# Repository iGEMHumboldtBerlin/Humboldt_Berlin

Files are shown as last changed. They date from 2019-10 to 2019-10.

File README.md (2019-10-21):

# Humboldt_Berlin

README

The openPBR is a low-cost, easy to assemble and reliable option to cultivate phototrophic organisms. We have developed it as an open-source platform to operate as you need it. It comes in several setups, from nine cultivation vessels to three flat panels with a minimum width of 15 mm and up to a volume of 190 ml. It provides users with the ability to measure optical density at wavelengths from 400 nm to 800 nm, online and provides a .csv file output. All parts are openly available and even gas supply is exactly adjustable through a rotameter, depending on the needs of your organism and setup. We want to offer scientists a simple and versatile cultivation platform.

################
Design and development by Paul Herrmann

The openPBR is controlled by one single Arduino script, which enables by varying 9 variables full control of all parameters. 
These variables are for light, pumping time (one for each pump), interval of measurement and wished OD of dilution.

To get the output of the openPBR use the free serial log program PuTTY: https://www.chiark.greenend.org.uk/~sgtatham/putty/latest.html and save as a .csv.

The current code on _v0.1 is for 3 sensors. 

User manual:
1. Start the Arduino IDE open the openPBR_control
2. Select the COM of the Arduino
3. Choose your settings:

For the light color and intensity set the value between 0 and 255 in line White line 91, Red line 92,Green 93,Blue 94 for the according color.

To adjust the interval of measurement, type a value between 30000 and 1000000 in line 99. This value is given in milliseconds so one minute is 60000 milliseconds.

To adjust the run time of the pumps set the value in line 100 from (milliseconds).
The value for the OD that starts the pumping can be set for every chamber starting at line 383. (example OD 1 [a.u.] = 0.95v on Vout of opt101. Divide 1024 by 5 volt times the Vout value you want to dilute the culture by)
 
4. Upload the code to the Arduino
5. Start PuTTy and Select the COM of the Arduino
6. Choose the output file folder and and give your .csv a name.
7. Start PuTTy logging.
8. Close PuTTy and the values are stored in the .csv file.

How to convert the values into OD, see Calibration openPBR DIY step by step on GitHub.

For help contact: igemberl@hu-berlin.de 

README

The openPBR is a low-cost, easy to assemble and reliable option to cultivate phototrophic organisms. We have developed it as an open-source platform to operate as you need it. It comes in several setups, from nine cultivation vessels to three flat panels with a minimum width of 15 mm and up to a volume of 190 ml. It provides users with the ability to measure optical density at wavelengths from 400 nm to 800 nm, online and provides a .csv file output. All parts are openly available and even gas supply is exactly adjustable through a rotameter, depending on the needs of your organism and setup. We want to offer scientists a simple and versatile cultivation platform.

################
Design and development by Paul Herrmann

The openPBR is controlled by one single Arduino script, which enables by varying 9 variables full control of all parameters. 
These variables are for light, pumping time (one for each pump), interval of measurement and wished OD of dilution.
To get the output of the openPBR the free serial log program PuTTY: https://www.chiark.greenend.org.uk/~sgtatham/putty/latest.html

User manual:

The current code on _v0.1 is for 3 sensors. 

1. Start the Arduino IDE open the openPBR_control
2. Select the COM of the Arduino
3. Choose your settings:

For the light color and intensity set the value between 0 and 255 in line 91 for the according color.

brightnessWhite = 150;
brightnessRed = 150;
brightnessGreen = 150;
brightnessBlue = 150; 

To adjust the interval of measurement change:

const long interval = 10*60*1000; // 10 minutes x 60 sec * 1000 milli 

To adjust the run time of the pumps set the value in line 100 from 

const int pumpTime = 5000; // time the pump is running

The value for the OD that starts the pumping can be set for every chamber starting at line 383. (example OD 1 [a.u.] = 0.95v on Vout of opt101. Divide 1024 by 5 volt times the Vout value you want to dilute the culture by)
 
4. Upload the code to the Arduino
5. Start PuTTy and Select the COM of the Arduino
6. Choose the output file folder and and give your .csv a name.
7. Start PuTTy logging.
8. Close PuTTy and the values are stored in the .csv file.

How to convert the values into OD, see Calibration openPBR DIY step by step on GitHub.

For help contact: igemberl@hu-berlin.de

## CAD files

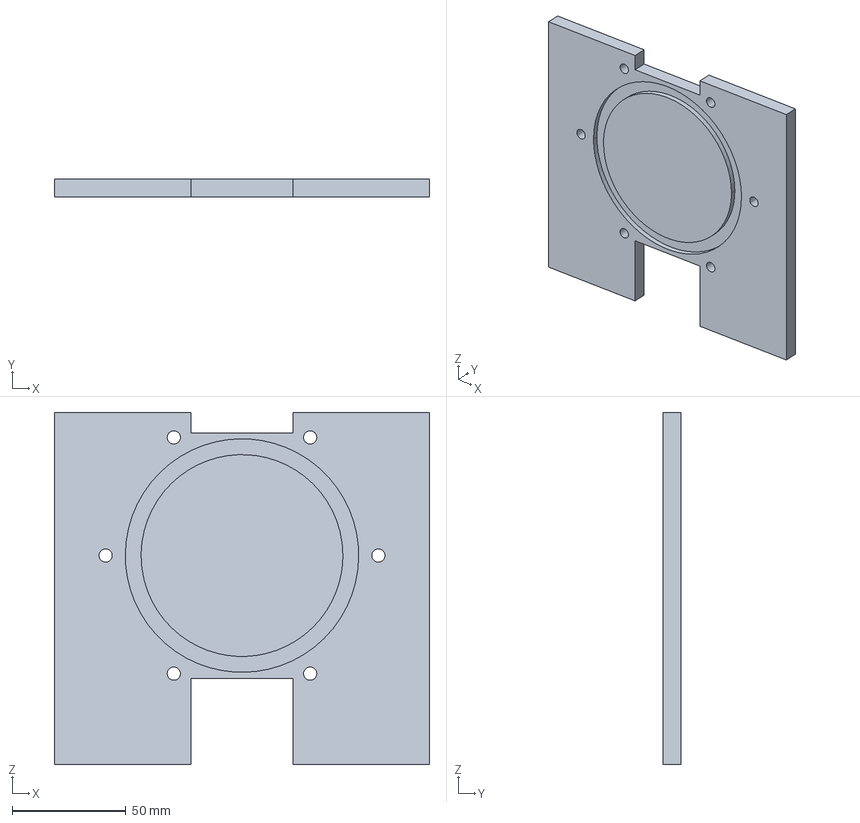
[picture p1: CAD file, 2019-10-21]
Laser cut files/Flat panel groove_02.stp
165.0 x 8.00 x 155.0 mm

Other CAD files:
CAD Models/openPBR_ laser cut_v0.1.dwg
Laser cut files/openPBR_lasercut_v0.1.dwg

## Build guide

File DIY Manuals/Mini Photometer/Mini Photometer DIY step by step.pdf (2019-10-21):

Introduction

To perform our needed functions, we build a small low-cost DIY photometer which can measure the optical density (OD) at 680 nm or any other wavelength in the visible spectrum. The photometer is designed to not only work inside our cultivation setup, but can also be used as a stand-alone solution for OD measurement.

Photometer
This is a small do it yourself photometer, using the light sensor Opt101 from Texas Instruments. It measures the absorption at 680nm of a given solution or cell culture as optical density (OD).
Parts List:
- Monolithic linear ambient light sensor Opt101
- LED 680nm (or else in visible light)
- 2 standard cuvettes
- Arduino with USB cable
- 2x 1kohm, 2x 10ohm,1x 5kohm resistors (optional potentiometer)
- Cables
- Two steel plates 80x10x1mm with two 3mm holes and a 50mm slit.
- 3x 3mm screws and nuts.
- optional 1-2 spacer (12mm long steel pipe)
- Breadboard
- Cardboard box
Software:
- Arduino IDE
- Putty (for serial monitor to csv file)
- Code for the photometer

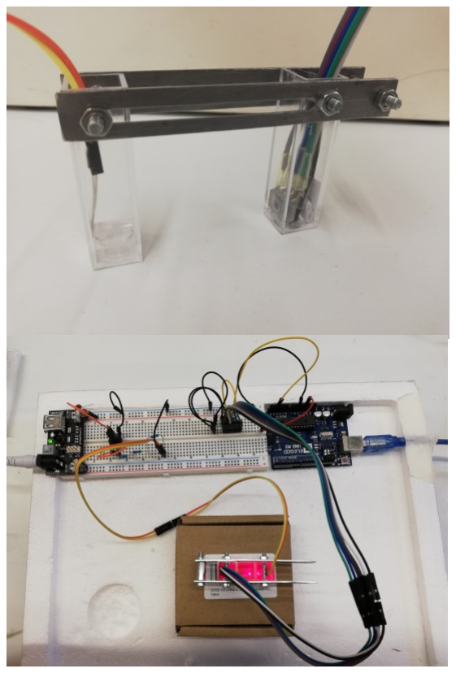
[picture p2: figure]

# Cost list and links:

LED680-02AU, 680 nm, 25 mW/sr, 4 mW at 20 mA, ±7°, 5 mm clear epoxy http://www.roithner-laser.com/datasheets/led_div/led680-series.pdf 3,98 Euro
OPT101 Lightsensor linear VIS IR Photodiode 300nm-1100nm 2,7-36V Sensor Modul https://www.amazon.de/gp/product/B07WHTF4S9/ref=ppx_yo_dt_b_asin_title_o00_s00?ie=UTF8&psc=1 (https://www.amazon.de/gp/product/B07WHTF4S9/ref=ppx_yo_dt_b_asin_title_o00_s00?ie=UTF8&psc=1) 4,97 Euro
ARDUINO UNO REV 3
https://www.amazon.de/Arduino-Uno-Rev-3-Mikrocontroller-Board/dp/B008GRTSV6/ref=sr_1_4?__mk_de_DE=%C3%85M%C3%85%C5%BD%C3%95%C3%91&keywords=Arduino&qid=1570469452&s=industrial&sr=1-4 (https://www.amazon.de/Arduino-Uno-Rev-3-Mikrocontroller-Board/dp/B008GRTSV6?__mk_de_DE=%C3%85M%C3%85%C5%BD%C3%95%C3%91&s=industrial) 17,89 Euro
Total: ~ 27 Euro

We would recommend buying an Arduino set with a lot of other fun parts and everything you need like cables and resistors.
ELEGOO UNO R3 Ultimate Starter Kit https://www.amazon.de/Elegoo-Vollst%C3%A4ndige-Ultimate-Tutorial-Mikrocontroller/dp/B01IHCCKKK?ref_=ast_sto_dp (https://www.amazon.de/Elegoo-Vollst%C3%A4ndige-Ultimate-Tutorial-Mikrocontroller/dp/B01IHCCKKK) 46,99 Euro

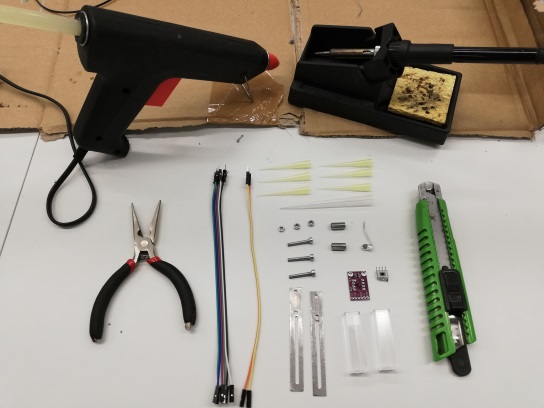
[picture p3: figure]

Tools:
- soldering iron
- Knife
- Tongs
- Hot glue (optional)

Assembling of the parts.
1.Prepare the LED attachment with a 1ml Pipet tip. Put the LED in the middle part of the pipet tip
that should be around 10mm long and stick in
to the cuvette. Paper on the sides helps to
center the LED.

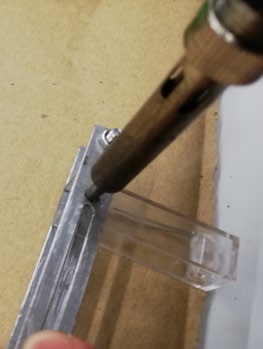
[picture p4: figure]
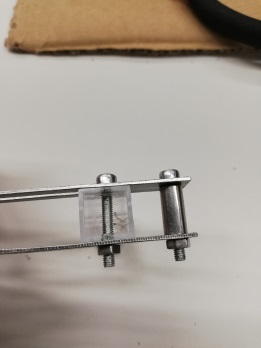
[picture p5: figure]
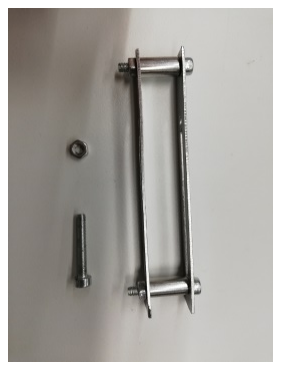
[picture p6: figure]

2. Assemble the cuvette holding and burn holes in the cuvettes with the soldering iron. Put the screw to the holes and fix them with the nuts.

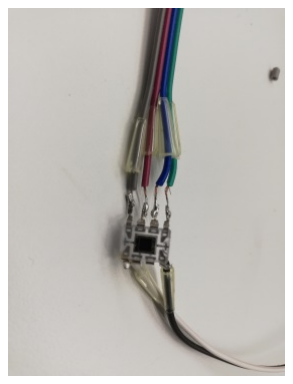
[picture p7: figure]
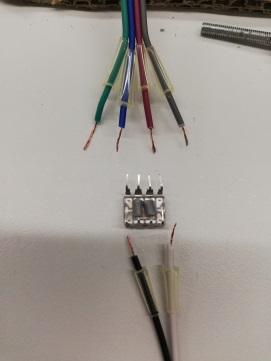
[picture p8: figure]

3. Prepare cables and something to protect the contacts for example 200µl pipet tips. Solder the cables to the Opt101.

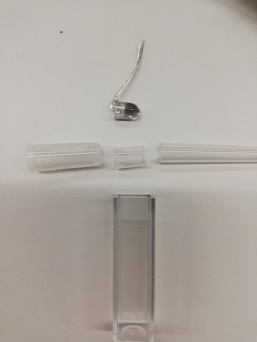
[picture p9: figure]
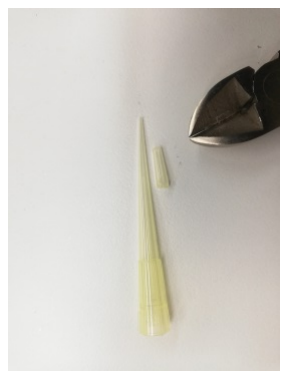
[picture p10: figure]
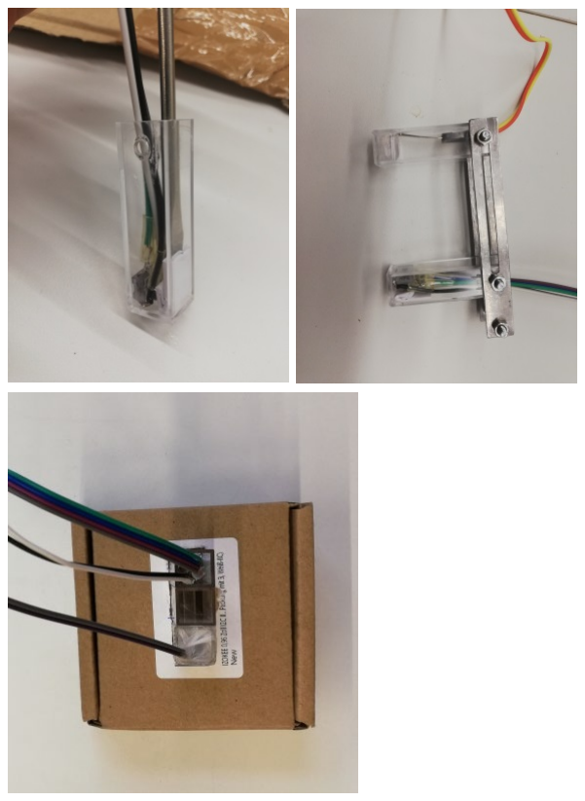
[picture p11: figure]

4. Insert the Opt 101 in to its cuvette and screw it in the cuvette holder. Add some paper so it stays in place and fits tight.
7. Cut out a hole in a cardboard box and put the photometer in.

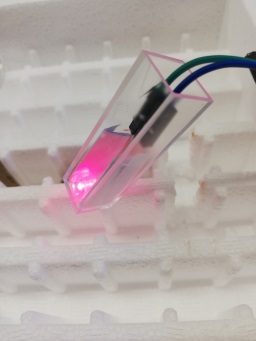
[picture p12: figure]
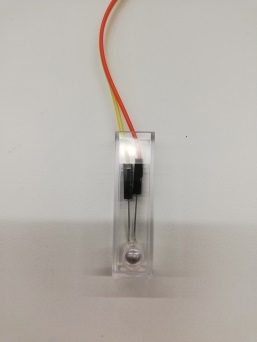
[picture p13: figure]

Wiring of the Opt101 to the Arduino. Connect the cables to the Opt101 as following: 1: green 5/3,3V (VCC)
3: black to GND
2: blue, 4: grey, 5: white over a 1M ohm resistor to Output 8: violet to GND
6 and 7 to nothing.

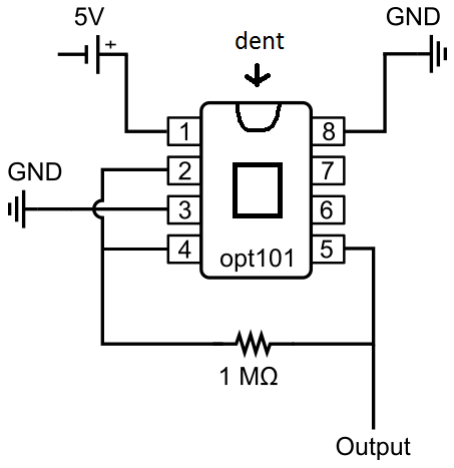
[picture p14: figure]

The sensor has a dent on one side this shows the orientation. It should look like this:

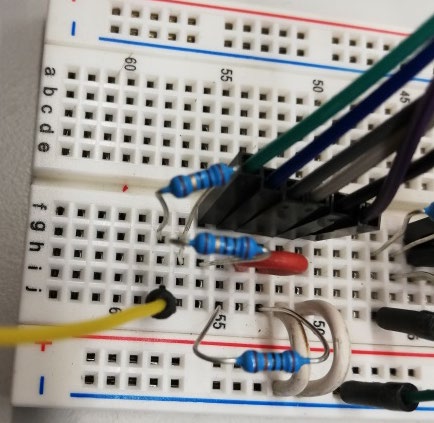
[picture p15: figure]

- Connect the Output (orange) and
a cable to monitor the current (red) to an analog pin (A0, A3) as well as the 5V (yellow) to the Arduino. Connect a cable (black) to GND.

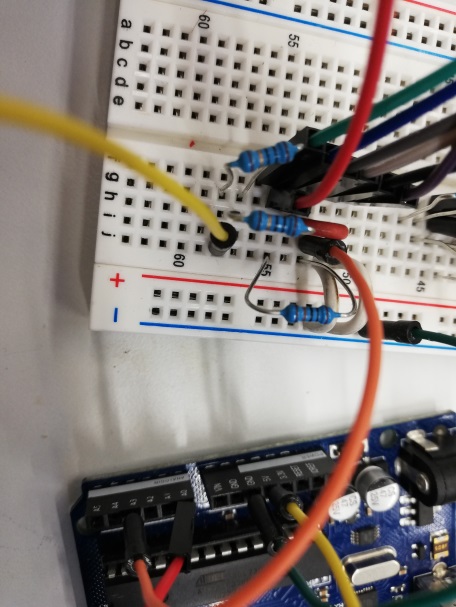
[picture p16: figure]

- For the 680nm LED connect a cable to 5V and put one 1 kohm and a 5 kohm resistor in a row to generate ~1.4 kohm resistance. This depends on the distance between LED and sensor as to the LED itself so it will differ from setup to setup. You can also put a Potentiometer instead of the resistor to find out which resistance fits for your setup. But don’t give the LED 5V, OR IT WILL BURST!

## Calibration of the Opt101

Prepare a dilution series of your Algae in this case C. reinhardtii. And measure it with a at 680 nm photometer.

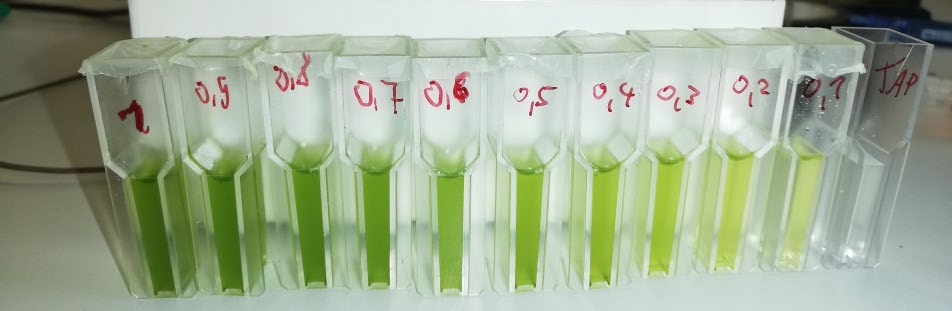
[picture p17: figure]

1. To calibrate the sensors set up a decadal dilution series of a given OD (from a reference photometer) from OD 2.5 down do OD 0.1.
2. Set the interval in the openPBR_control to 30 seconds
3. Start PuTTY and measure a single data point for each step of the dilution.
4. Include the data in to a excel file.

In order to get a net voltage, you need to subtract the output value from the input value. Subtract the Vout values from the Vin values and plot them against the reference OD from your photometer. Then perform a logarithmic fit (Fig. 1)

Your equation should look something like this: ∆VV = aa ∗ log(OOOO) + bb

In our example we got a = 0.496 and b = 4.389.

In this case, y is the voltage ∆V and x the OD.

To get the OD from your measured values, solve your equation for x:

# xx = ee

# ∆VV−bb

aa

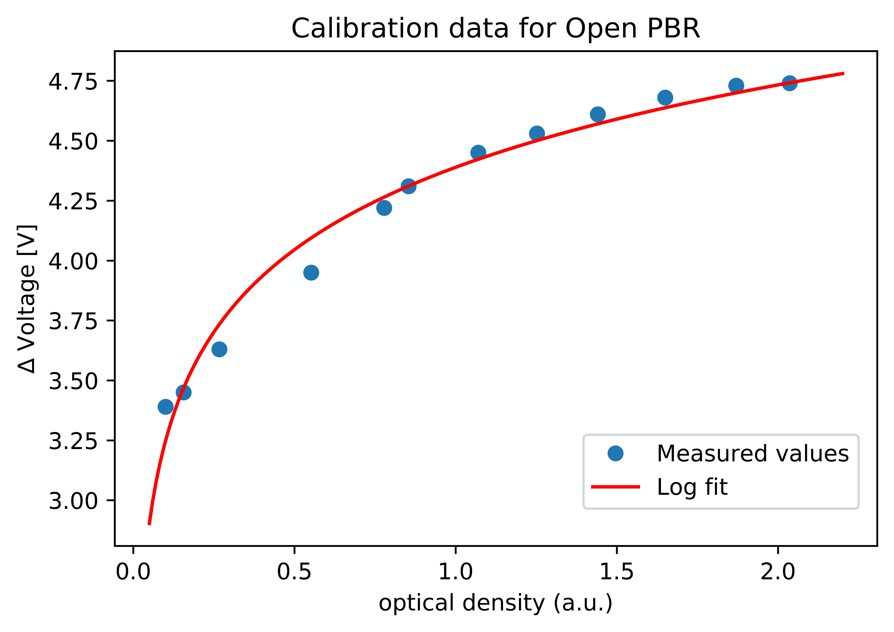
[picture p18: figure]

Image 1:Measured OD with reference photometer against measured ∆V with openPBR
After the calibration, we measured other random samples both with our reference photometer (Expected OD) and with openPBR (Figure 2).

We also plotted the “ideal correlation”, meaning expected = measured, in order to get an idea of how good the openPBR measurements are.

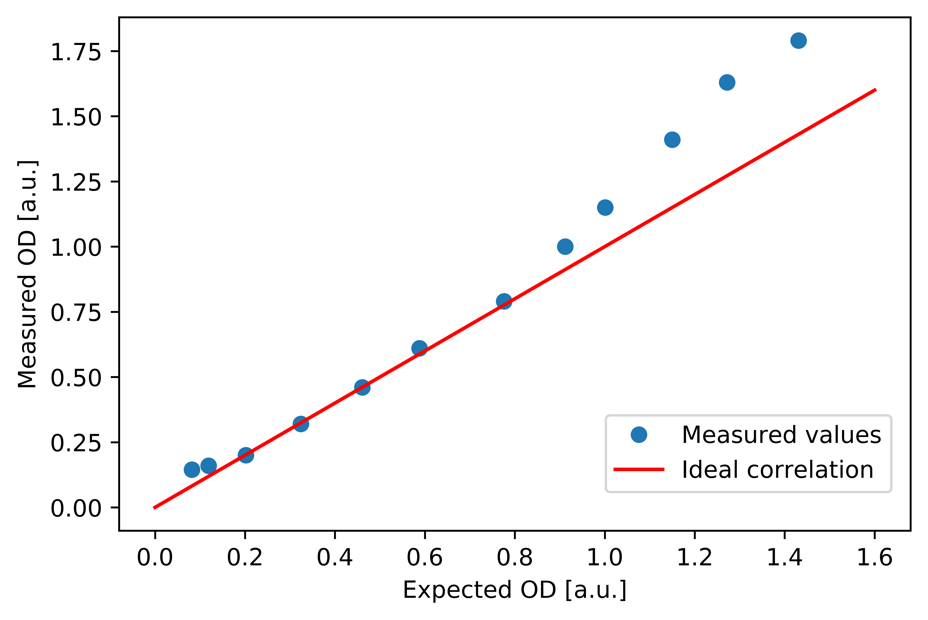
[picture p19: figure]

Figure 2: Expected OD values from reference photometer plotted against openPBR measurements with an “ideal correlation” of x = y

From this we can conclude that, while the openPBR measurements between OD = 0 and OD = 1 are quite reliable, further calibrating points are needed in order to improve the range beyond OD = 1.

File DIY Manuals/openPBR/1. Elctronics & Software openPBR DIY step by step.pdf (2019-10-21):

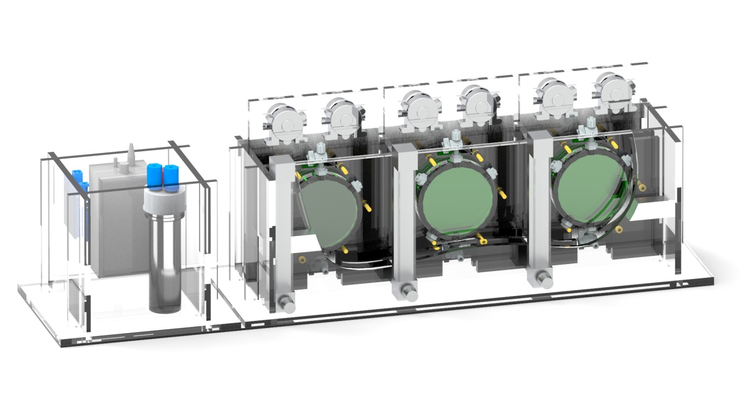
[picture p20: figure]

Electronics (openPBR)
The openPBR is controlled by an Arduino AT Mega 2560.The whole system is powered by a 12V network adapter. The gas supply system and LED panel run on 12V. A voltage regulator (LM317) is providing the sensors and pumps with 5V. In this first iteration the whole wiring is placed on one standard breadboard so it is possible to rebuild this setup with a simple Arduino starter kit and some additional parts like MOSFETs and the LM317. In future we will produce a shield which will make the workflow with this setup even simpler.
Parts list:

ELEGOO UNO R3 Ultimate Starter Kit, 46,99 Euro https://www.amazon.de/Elegoo-Vollst%C3%A4ndige-Ultimate-Tutorial-Mikrocontroller/dp/B01IHCCKKK?ref_=ast_sto_dp (https://www.amazon.de/Elegoo-Vollst%C3%A4ndige-Ultimate-Tutorial-Mikrocontroller/dp/B01IHCCKKK)
Arduino Mega 2560, ATmega 2560 34,40 Euro https://www.reichelt.de/arduino-mega-2560-atmega-2560-usb-arduino-megap119696.html?&trstct=pos_0 (https://www.reichelt.de/arduino-mega-2560-atmega-2560-usb-arduino-mega-p119696.html?&trstct=pos_0)
Prices for MOSFET and LM317 are in the Pumps DIY step by step PDF and LED Total: 81,39

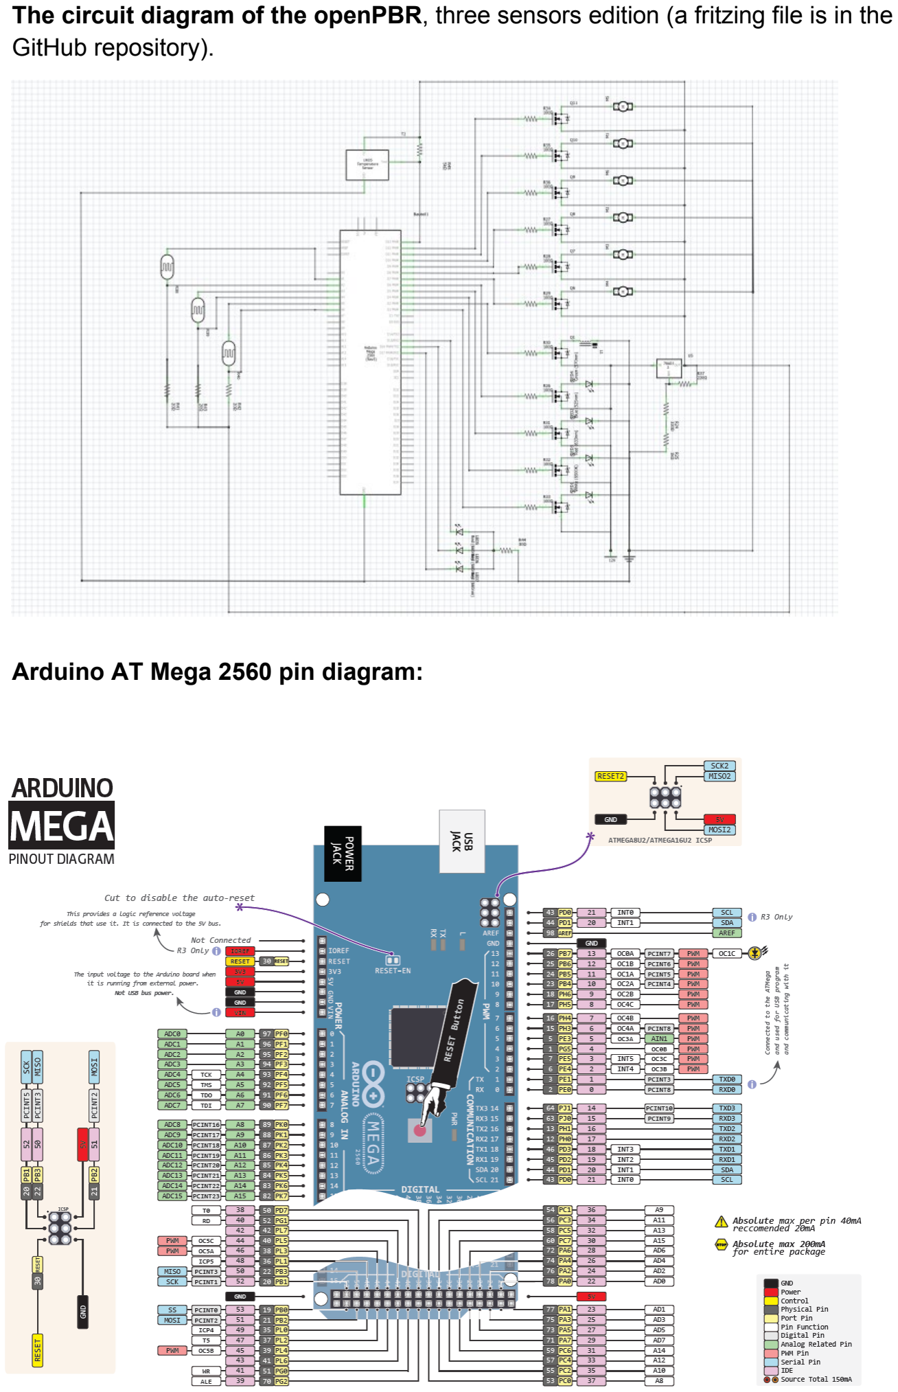
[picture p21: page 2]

The circuit diagram of the openPBR, three sensors edition (a fritzing file is in the GitHub repository).

Arduino AT Mega 2560 pin diagram:

Software
The Open PBR is controlled by one single Arduino script, which enables by varying 9 variables full control of all parameters.
These variables are for light, pumping time (one for each pump), interval of measurement and wished OD of dilution.
To get the output of the openPBR the free serial log program PuTTY: https://www.chiark.greenend.org.uk/~sgtatham/putty/latest.html (https://www.chiark.greenend.org.uk/%7Esgtatham/putty/latest.html)

User manual:
1. Start the Arduino IDE open the openPBR_control
2. Select the COM of the Arduino
3. Choose your settings:
- For the light color and intensity set the value between 0 and 255 in line 91,92,93,94 for the according color.
- To adjust the interval of measurement, type a value between 30000 and 1000000 in line 99. This value is given in milliseconds so one minute is 60000 milliseconds.
- To adjust the time for the pumps to run also in milliseconds, line 100.
- The value for the OD that starts the pumping can be set for every chamber starting at line 383.
4. Upload the code to the Arduino
5. Start PuTTy and Select the COM of the Arduino
6. Choose the output file folder and and give your .csv a name.
7. Start PuTTy
8. Close PuTTy and the values are stored in the .csv file

To convert the values into OD see: Sensors openPBR DIY step by step on GitHub

For help contact: igemberl@hu-berlin.de

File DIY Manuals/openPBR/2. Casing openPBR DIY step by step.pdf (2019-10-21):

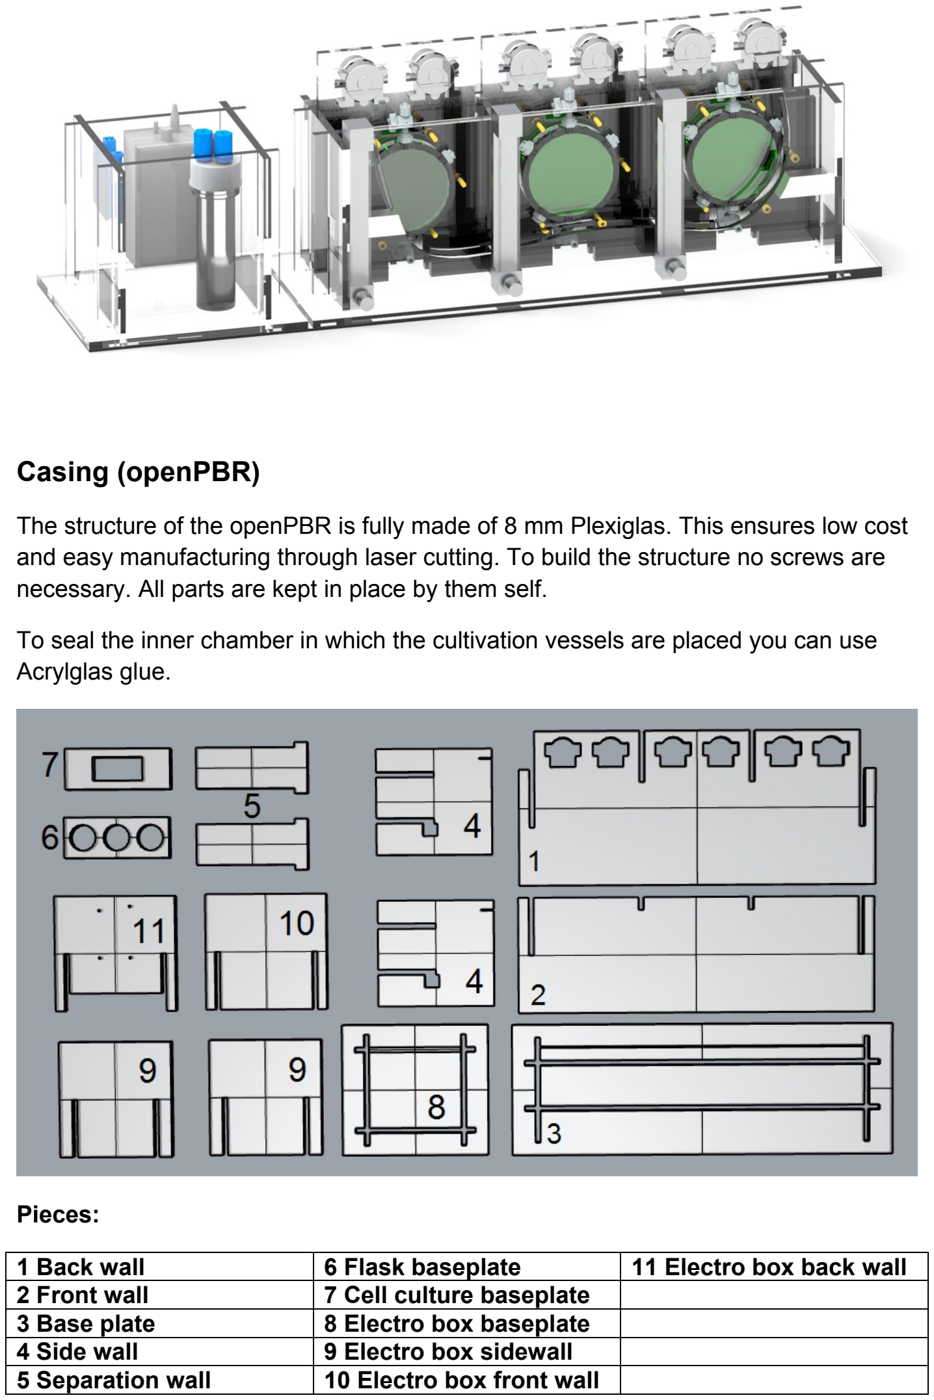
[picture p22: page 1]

### Casing (openPBR)

The structure of the openPBR is fully made of 8 mm Plexiglas. This ensures low cost and easy manufacturing through laser cutting. To build the structure no screws are necessary. All parts are kept in place by them self.
To seal the inner chamber in which the cultivation vessels are placed you can use Acrylglas glue.

Pieces:
1 Back wall | 6 Flask baseplate | 11 Electro box back wall
2 Front wall | 7 Cell culture baseplate
3 Base plate | 8 Electro box baseplate
4 Side wall | 9 Electro box sidewall
5 Separation wall | 10 Electro box front wall

Price:
We bought Plexiglas from http://www.gruenberg-kunststoffe.de/produkte/acrylglaspmma/ (http://www.gruenberg-kunststoffe.de/produkte/acrylglas-pmma/) but you can easily use the laser cut files and order the parts at https://www.formulor.de/ or similar provider of laser cutting service.
> Acrylglas GS colorless
> 1 Stk 783 x 216 x 8 mm | 15,85 €
> 1 Stk 580 x 260 x 8 mm | 14,10 €
> 1 Stk 580 x 200 x 8 mm | 10,95 €
> 2 Stk 230 x 200 x 8 mm | 4,45 € pro Stk
> 2 Stk 210 x 200 x 8 mm | 4,10 € pro Stk
> 2 Stk 200 x 190 x 8 mm | 3,70 € pro Stk
> 5 Stk 180 x 130 x 8 mm | 2,35 € pro Stk
> 2 Stk 190 x 150 x 8 mm | 2,85 € pro Stk
ACRIFIX ® 1R0192 PMMA, Acrylglas/Plexiglas ® ~ 10 Euro https://www.amazon.de/ACRIFIX-Acrylglas-Plexiglas-Polystyrol-Polycarbonat/dp/B00TIY449W/ref=sr_1_1?__mk_de_DE=%C3%85M%C3%85%C5%BD%C3%95%C3%91&keywords=acrifix&qid=1571499264&s=diy&sr=1-1 (https://www.amazon.de/ACRIFIX-Acrylglas-Plexiglas-Polystyrol-Polycarbonat/dp/B00TIY449W?__mk_de_DE=%C3%85M%C3%85%C5%BD%C3%95%C3%91&s=diy) Total: 78 euro
Remove the foil from the Plexiglas and stack all plates in to each other. Part 1-7 are for the main chamber and 7-11 are the electricity box.

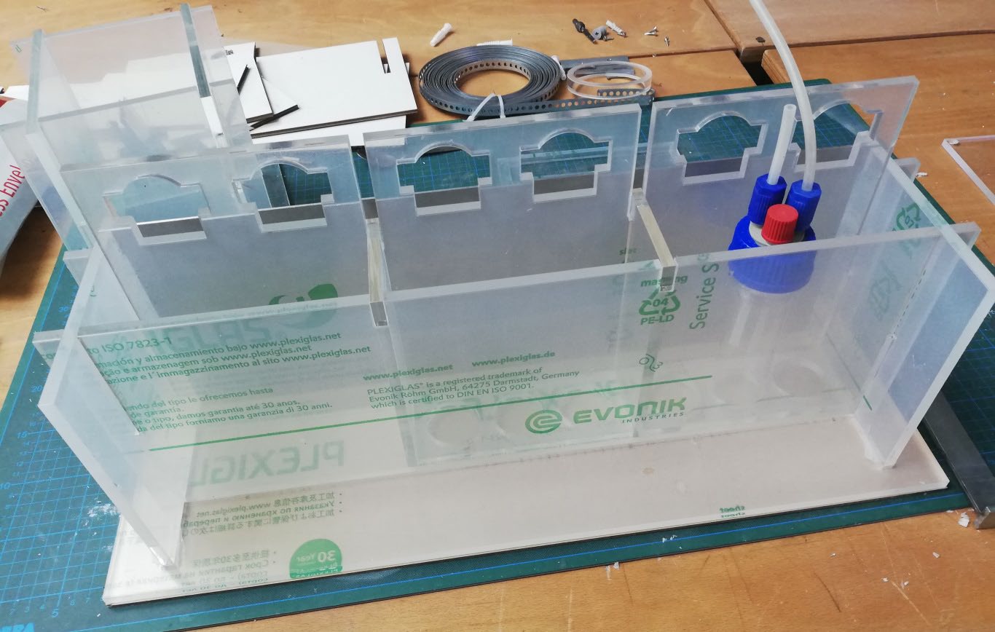
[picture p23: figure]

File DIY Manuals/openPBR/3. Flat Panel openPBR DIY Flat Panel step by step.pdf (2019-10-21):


### Flat Panel (Open PBR) Fully Autoclaveable!

This do it yourself tutorial is for the Open PBR Flat Panel setup.
This cultivation vessel can be used as single or in a triplicate cultivation setup. It has a volume of 95 ml up to 195 ml. In the smallest variant it is just 15 mm thick which enables high density cultivation. All parts on this vessel is autoclaveable at 121°C for 40 min at 4 bar.

This protocol is fairly difficult but you can massage us at igemberl@hu-berlin.de for guidance. We bought about 2 m of Plexiglas pipe 90x102, which is the most expensive part on this setup, and could send you the ring thickness of your choice by post.

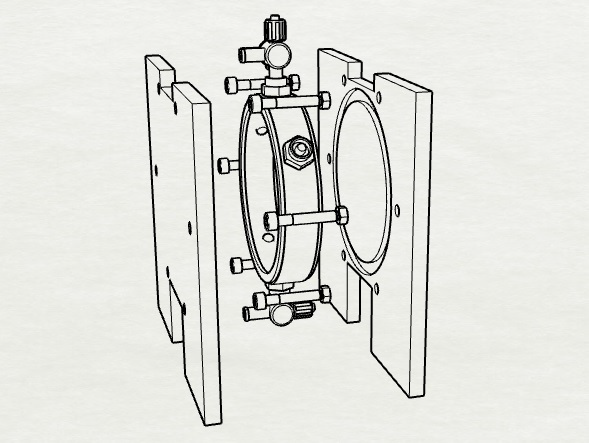
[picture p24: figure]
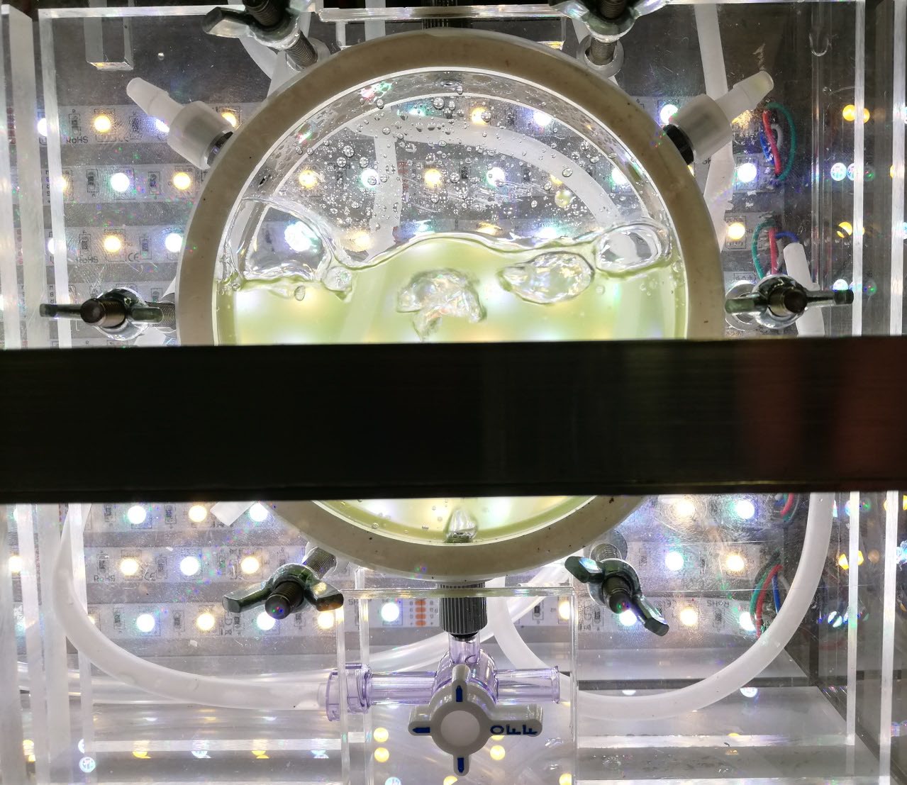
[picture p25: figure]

## Parts:

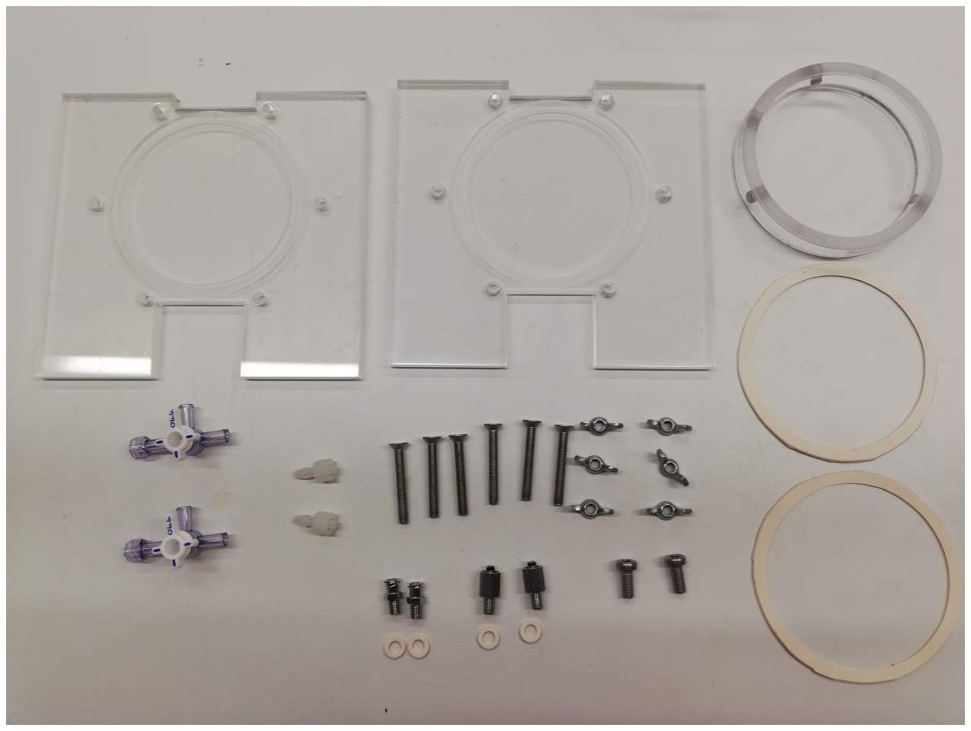
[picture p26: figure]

- Two Plexiglas (PMMA) plates 8mm thick, 155x165mm ~ 5 Euro
- Plexiglas ring 17x90x102mm ~ 2 euro http://www.gruenberg-kunststoffe.de/produkte/acrylglas-pmma/
- 6x M4 flat head screws 40 mm long
- 6x M4 butterfly nut
- 2x M6 screws (optional for none turbidostatic mode) ~5 Euro
- 2x Luerlock M6 female adapter https://www.droh.de/produkt/6184-adapter-aus-messing-vernickelt-anschluesse-luerlock-weiblich-m5-gewinde (https://www.droh.de/produkt/6184-adapter-aus-messing-vernickelt-anschluesse-luer-lock-weiblich-m5-gewinde) 3,10 Euro
- 2x Luerlock M6 male adapter https://www.droh.de/produkt/6198-adapter-aus-messing-vernickelt-anschluesse-luerlock-maennlich-m6-gewinde (https://www.droh.de/produkt/6198-adapter-aus-messing-vernickelt-anschluesse-luer-lock-maennlich-m6-gewinde) 4,80 Euro
- 2x Luerlock threeway stopcock https://www.coleparmer.de/i/cole-parmer-stopcocks-with-luer-connections-3-waymale-lock-non-sterile-10-pk/3060002 (https://www.coleparmer.de/i/cole-parmer-stopcocks-with-luer-connections-3-way-male-lock-non-sterile-10-pk/3060002) x10 19,65 Euro
- 2x Luerlock female
- https://www.coleparmer.de/i/cole-parmer-male-luer-with-lock-ring-x-1-4-id-hose-barbnylon-25-pk/ (https://www.coleparmer.de/i/cole-parmer-male-luer-with-lock-ring-x-1-4-id-hose-barb-nylon-25-pk/) x25 for 7,50 Euro
- 2x silicone rings 2x90x102mm (self-made from 2mm silicone mat) https://www.amazon.de/Halnziye-Termico-Grau-Silicon-Thermal/dp/B07HP87HJH 15 Euro for 50x50mm

Total: 62,40 Euro
For three Flat Panel: 87,80 Euro

How to build it, step by step;

Laser cut and CNC files are in the Github Open PBR folder.

Step 1: Plexiglas: After laser cutting the edges and holes in to the two flat panel pieces you have use a CNC milling machine with a 8mm drill to mill 3 mm deep rings out of the glass. Then use a drill to make the holes suitable for M6 screws and widen the holes for flat head screws. These will ensure a tight seal of the flat panel.

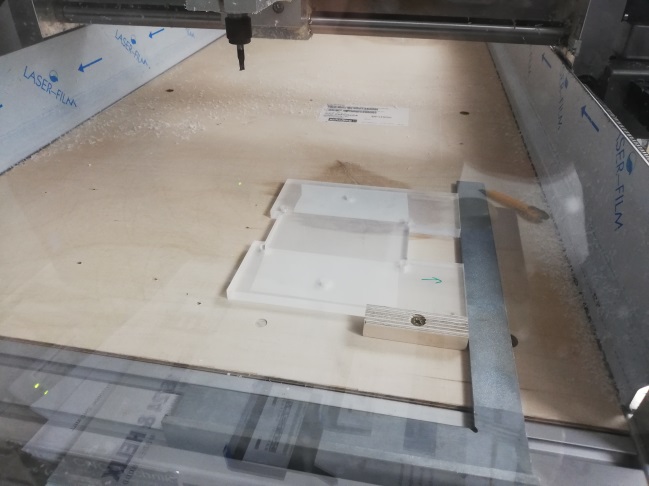
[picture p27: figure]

Step 2: Rings:

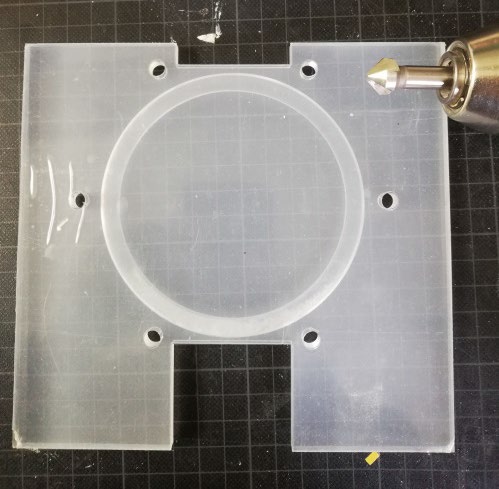
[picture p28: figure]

The volume of this flat panel setup is determined by the thickness of the ring between the Plexiglas walls. For the 95ml volume setup the ring is 17 mm thick. On each side 1 mm will sit in the previously milled groove. For bigger volumes cut rings as you like.
Drill six M6 holes, for the Luerlock valves, into the ring. Two holes opposite of each other and two in a 35° angel from the equator.
Detailed construction drawing is in the Github folder.

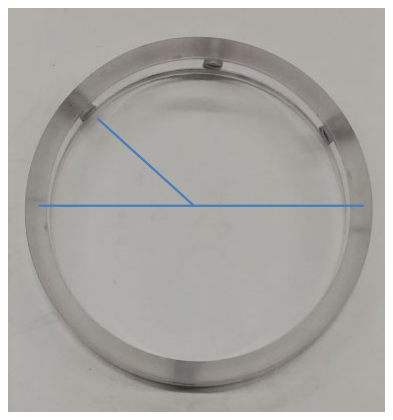
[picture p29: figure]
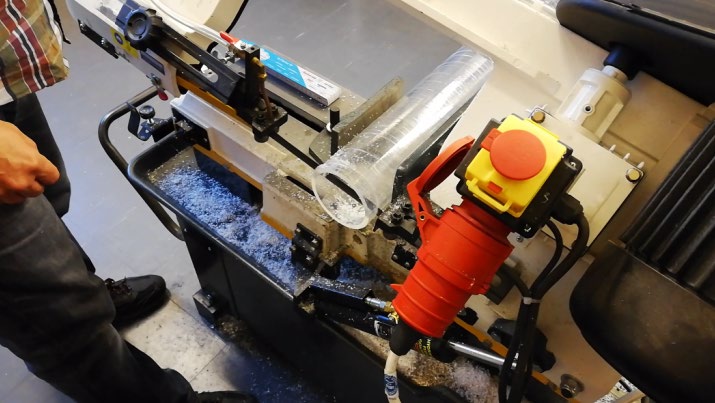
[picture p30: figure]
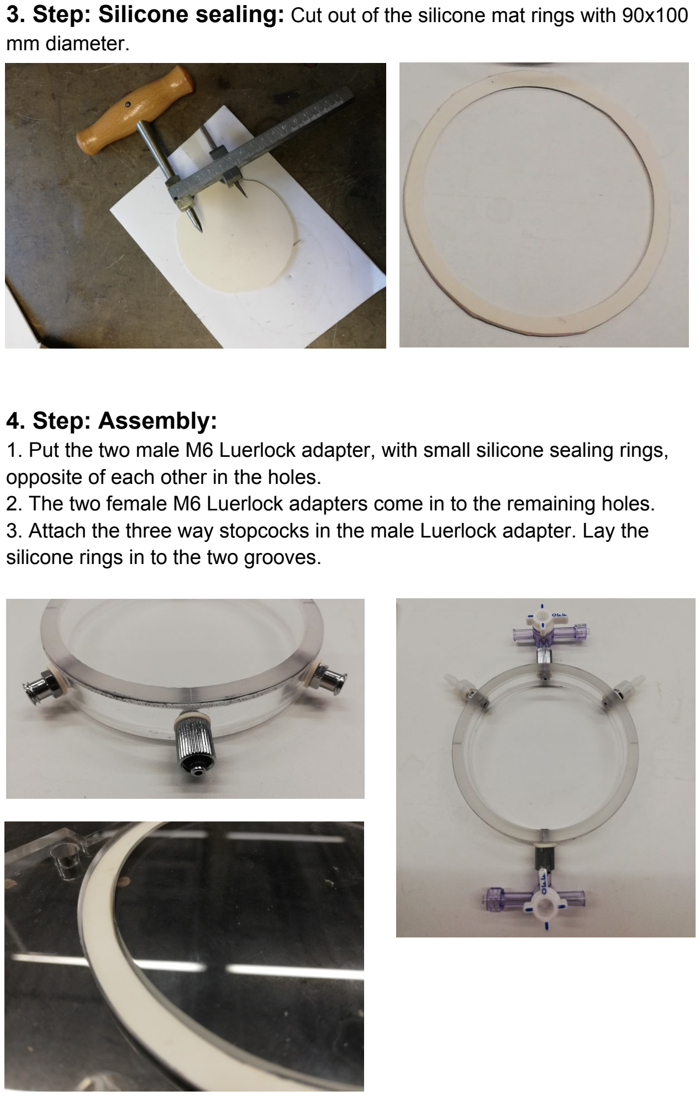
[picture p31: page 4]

### 3. Step: Silicone sealing: Cut out of the silicone mat rings with 90x100

mm diameter.

### 4. Step: Assembly:

1. Put the two male M6 Luerlock adapter, with small silicone sealing rings, opposite of each other in the holes.
2. The two female M6 Luerlock adapters come in to the remaining holes.
3. Attach the three way stopcocks in the male Luerlock adapter. Lay the silicone rings in to the two grooves.

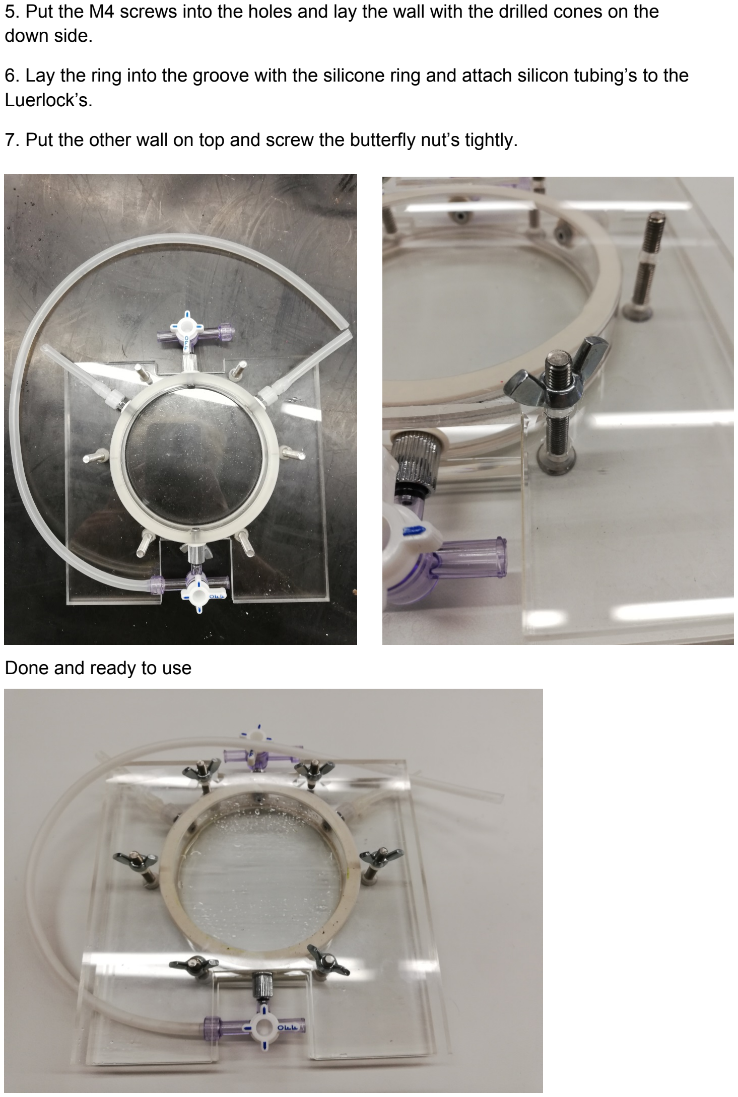
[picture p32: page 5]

5. Put the M4 screws into the holes and lay the wall with the drilled cones on the down side.
6. Lay the ring into the groove with the silicone ring and attach silicon tubing’s to the Luerlock’s.
7. Put the other wall on top and screw the butterfly nut’s tightly.

Done and ready to use

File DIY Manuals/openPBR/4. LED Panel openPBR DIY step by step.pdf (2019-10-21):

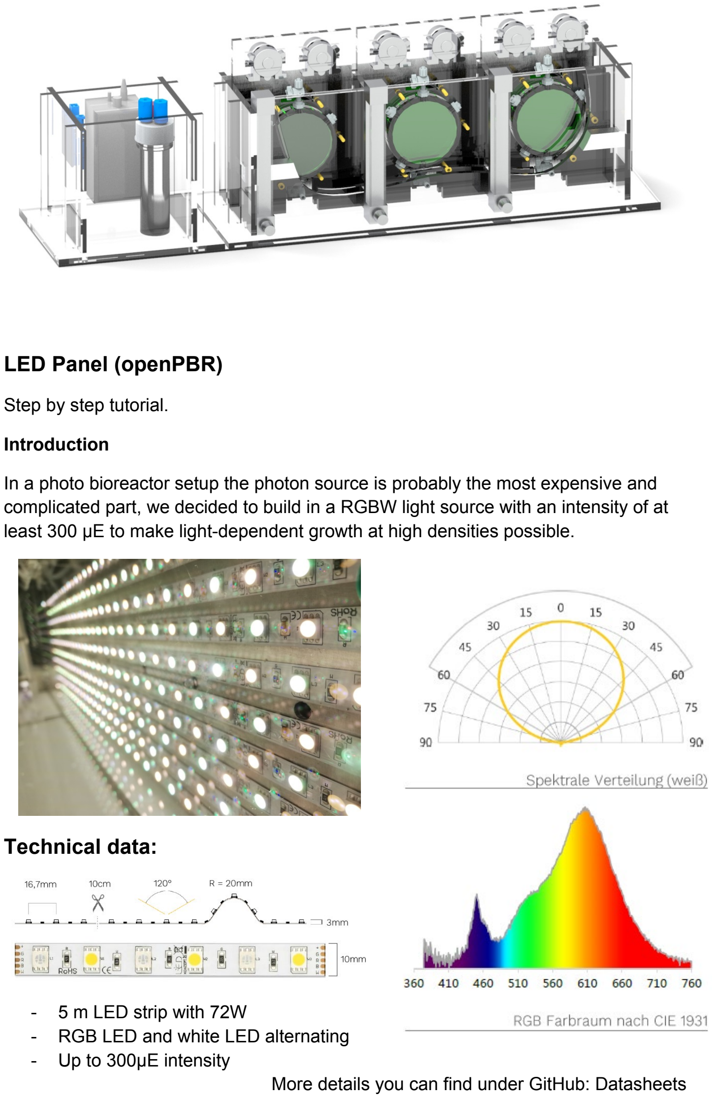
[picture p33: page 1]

### LED Panel (openPBR)

Step by step tutorial.
Introduction
In a photo bioreactor setup the photon source is probably the most expensive and complicated part, we decided to build in a RGBW light source with an intensity of at least 300 µE to make light-dependent growth at high densities possible.

### Technical data:

- 5 m LED strip with 72W
- RGB LED and white LED alternating
- Up to 300µE intensity
More details you can find under GitHub: Datasheets

Parts list:
- 5 m RGBW LED strip 79,90 Euro https://www.led-konzept.de/RGBW-LED-Streifen-12V-72W-pro-5m-RGB-warmweiss-500cm-mit-Litzenanschluss (https://www.led-konzept.de/RGBW-LED-Streifen-12V-72W-pro-5m-RGB-warmweiss-500cm-mit-Litzenanschluss)
- 120W Power adapter 64,49 Euro https://www.led-konzept.de/MeanWell-LED-Netzteil-HLG-120H-12B-12V-120W-IP67
- Aluminium Plate 57 x 175 x 2 mm ~ 2 Euro
- 4x N-Channel MOSFET 0,67 Euro https://www.reichelt.de/mosfet-n-ch-60v-50a-110w-0-018r-to220-stp55nf06-p257486.html?r=1 (https://www.reichelt.de/mosfet-n-ch-60v-50a-110w-0-018r-to220-stp55nf06-p257486.html?r=1)
- 4x Aluminium cool bloc 0,83 Euro https://www.reichelt.de/kuehlkoerper-25-mm-alu-60-k-w-sot-32-to-220-sk-12-25-sa-32-p227995.html?&trstct=pos_0 (https://www.reichelt.de/kuehlkoerper-25-mm-alu-60-k-w-sot-32-to-220-sk-12-25-sa-32-p227995.html?trstct=pos_0)

Total:150,39

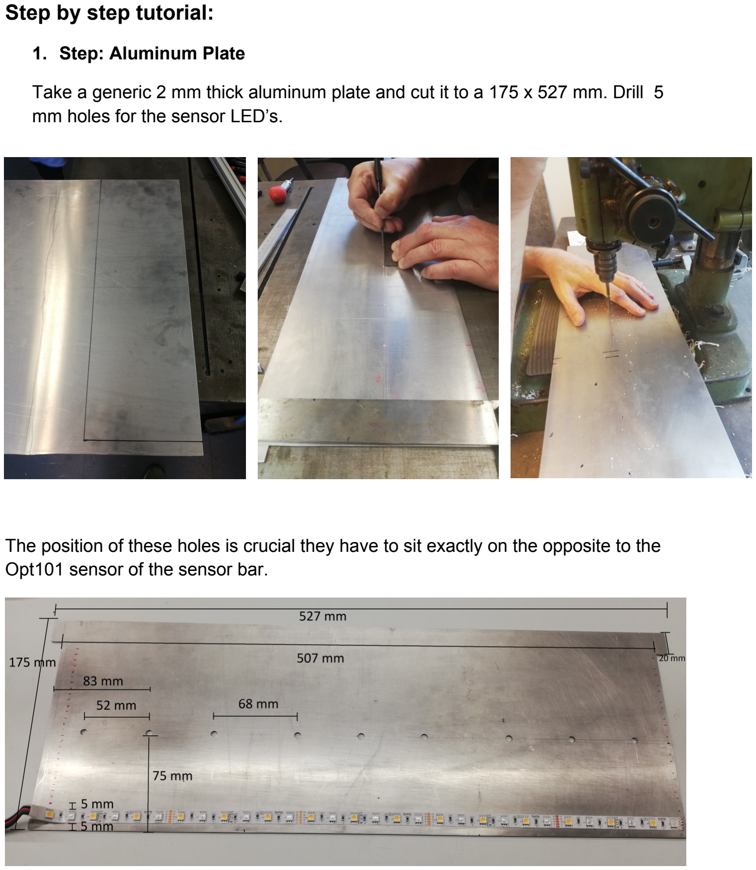
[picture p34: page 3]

### Step by step tutorial:

### 1. Step: Aluminum Plate

Take a generic 2 mm thick aluminum plate and cut it to a 175 x 527 mm. Drill 5 mm holes for the sensor LED’s.

The position of these holes is crucial they have to sit exactly on the opposite to the Opt101 sensor of the sensor bar.

### Step 2: LED stripes

- Stick the Led stripes with the tape of 50 cm in a distance of 5 mm.
- Solder the 5 pin contacts with cable to the next LED stripe.

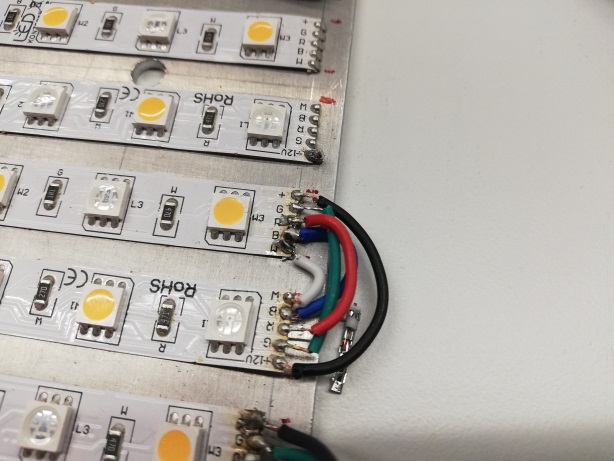
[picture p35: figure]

### Step 3: Electronics

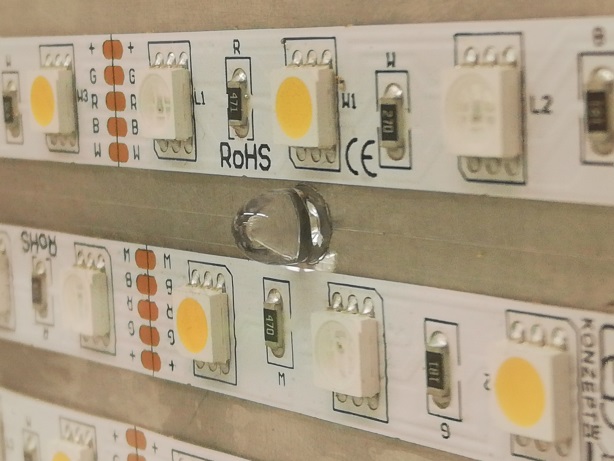
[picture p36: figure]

This LED panel is controlled by 4 N-Channel MOSFET. One MOSFET per color (R,G,B,W ). These transistors divide the 12V in to 255 steps in the Arduino code.
- Use 2 -3 mm screws to attach the cooling blocks to the MOSFET
- Connect G (Gate) with a 100 ohm resistor to your Arduino digital pin red pin 3, green pin 4, blue pin 5, white pin 6.
- Connect S (Source) to ground (-).
- Connect D (Drain) to each color cable of the LED.
- Connect the 12V (+) of the LED to the network adapter.

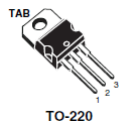
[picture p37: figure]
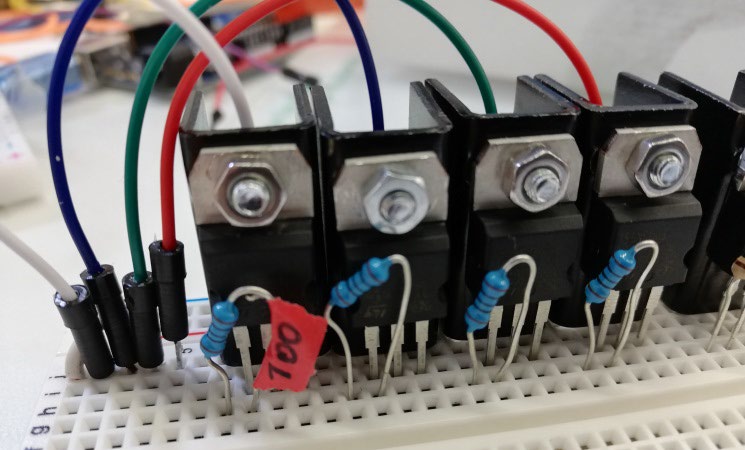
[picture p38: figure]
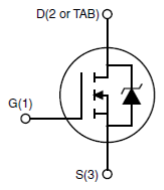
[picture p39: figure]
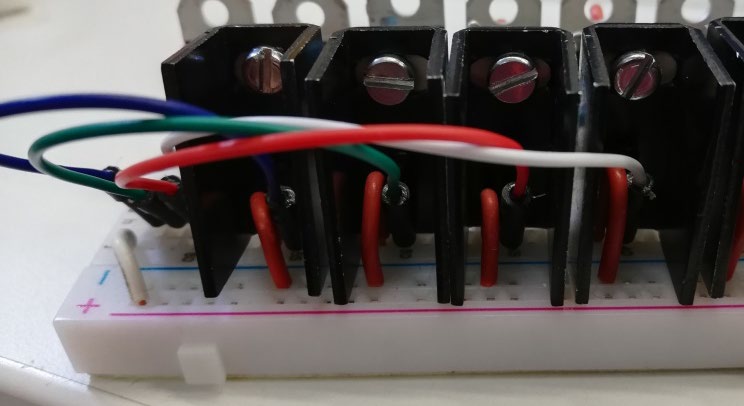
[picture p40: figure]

### 4. Calibration of the LED Panel

To determine the intensity of your LED panel us a µmol meter. Put the LED Panel in the casing of the Open PBR. Paint a point in a raster on the front wall, every 25 mm from top to bottom and every 80 mm. Measure the intensity at every point and plot them in to a graph. In the case of this LED panel the maximum intensity is 300 µmol/s*m² e.g. (300µE).

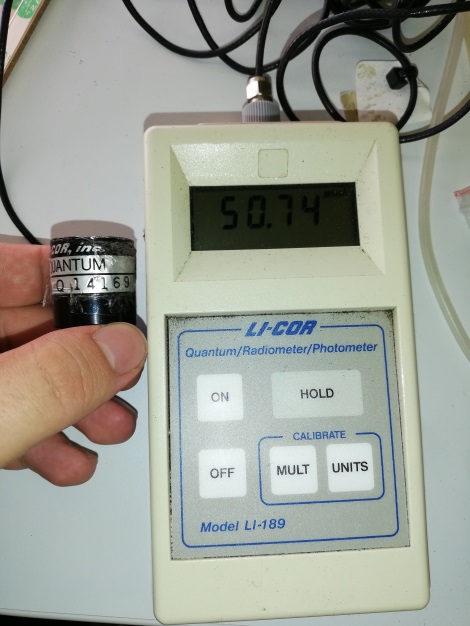
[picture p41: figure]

The software to control the LED’s you find in the openPBR_control software.

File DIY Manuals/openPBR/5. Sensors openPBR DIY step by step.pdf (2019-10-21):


## Sensor system (openPBR)

The sensory system of the openPBR consist of up to nine Opt 101 Monolithic linear voltage sensors and nine 680 nm LED’s. It is possible to use any LED in the linear area of the sensor thus measurements from 450 nm to 750 nm. And a temperature sensor to measure the water bath temperature.
1. Sensor rail
2. Opt 101
3. 680 nm LED
4. Calibration
5. Thermometer

Sensor rail of the openPBR Opt101:

Partlist:
- Monolithic linear ambient light sensor Opt101, 4,97

https://www.amazon.de/gp/product/B07WHTF4S9/ref=ppx_yo_dt_b_asin_title_o00_s00?ie=UTF8&psc=1 (https://www.amazon.de/gp/product/B07WHTF4S9/ref=ppx_yo_dt_b_asin_title_o00_s00?ie=UTF8&psc=1)
- x3 – x9LED 680 nm (or else in visible light), 3,89 Euro

http://www.roithner-laser.com/datasheets/led_div/led680-series.pdf
- Two 527 x 20 x 20 mm Aluminum angle rails 4,29 Euro https://www.amazon.de/GAH-Alberts-473631-Winkelprofil-Aluminiumsilberfarbig/dp/B002TYLFAE/ref=sr_1_3?__mk_de_DE=%C3%85M%C3%85%C5%BD%C3%95%C3%91&keywords=aluminium+winkel&qid=1571517375&s=diy&sr=1-3 (https://www.amazon.de/GAH-Alberts-473631-Winkelprofil-Aluminium-silberfarbig/dp/B002TYLFAE?__mk_de_DE=%C3%85M%C3%85%C5%BD%C3%95%C3%91&s=diy)
- DS18B20 digital temperature sensor 3,99 Euro https://www.amazon.de/DS18b20-Wasserdichter-Temperatursensor-Thermometer-Temperaturf%C3%BChler/dp/B01G1F2172/ref=sr_1_22?__mk_de_DE=%C3%85M%C3%85%C5%BD%C3%95%C3%91&keywords=DS18B20+digital+temperature+sensor&qid=1570473194&s=garden&sr=1-22 (https://www.amazon.de/DS18b20-Wasserdichter-Temperatursensor-Thermometer-Temperaturf%C3%BChler/dp/B01G1F2172?__mk_de_DE=%C3%85M%C3%85%C5%BD%C3%95%C3%91&s=garden)
- x3 - x9 standard cuvettes (generic lab stuff)
- 3-9 x 1kohm, 3x 10ohm resistors (optional potentiometer), (part of Arduino starter kit)
- 6 pin Cables (part of Arduino starter kit)
- 2x M3 30 mm long screws and nuts. ~ 1Euro

Total for 3 sensors units: 35.87 Euro
Total for 9 sensors units: 83,69 Euro


Step by step Tutorial:
Step 1: Sensor rail:
- Take two 527 x 20 x 20 mm long Aluminum angle rails and drill nine 5 mm holes in one of them. A longer rail is also possible up to 600 mm.
- The distance between the holes is similar to the hole position of the holes in the LED panel. 52 mm between the three holes of one chamber and 68 mm to the next chamber
- Drill two M3 holes in to the opposite side of the alu rail and two holes in to the remaining alu rail so that they can be connected with a M3 screw.

LED Aluminum plate:

Step 2: Assembly of Opt101 and Aluminum rail:


Wiring of the Opt101 to the Arduino. Connect the cables to the Opt101 as following:
- 1: Connect green 5/3,3V (VCC)
- 3: black to GND
- 2: blue, 4: grey, 5: white over a 1M ohm resistor to Output
- 8: violet to GND
- 6 and 7 to nothing.


- The sensor has a dent on one side this shows the orientation.
- Connect the Output (orange) and a cable to monitor the current


- Connect (red) to an analog pin
(A0, A3) as well as the 5V
(yellow) to the Arduino.
- Connect a the black to GND.


- Solder the Opt 101 as seen below to a six pin cable.


- Stick the Opt101 in to a standard cuvette and make
sure the sensor is lying flat on the inner surface. Adjust its position with a folded piece of paper.
- Use hot glue to fix the cuvette in the aluminum rail. It is crucial that the sensor sits exactly in the center of the hole on the rail.


- Fit all cables into the rail and close it with the two screws and nuts.

Step 3: 680 nm LED
- Solder cable to the LEDs put them into the holes of


- Connect the 680 nm LED ground cable to ground with three 10 ohm resistors in row to 5V (-).
- Connect the (+) cables of the LEDs to a digital Pin of the Arduino.


Software for the sensors is in the openPBR control Software.

## Step 4: Calibration of the Opt101

Prepare a dilution series of your Algae in this case C. reinhardtii. And measure it with a at 680 nm photometer.


1. To calibrate the sensors set up a decadal dilution series of a given OD (from a reference photometer) from OD 2.5 down do OD 0.1.
2. Set the interval in the openPBR_control to 30 seconds
3. Start PuTTY and measure a single data point for each step of the dilution.
4. Include the data in to a excel file.

In order to get a net voltage, you need to subtract the output value from the input value. Subtract the Vout values from the Vin values and plot them against the reference OD from your photometer. Then perform a logarithmic fit (Fig. 1)

Your equation should look something like this: ∆VV = aa ∗ log(OOOO) + bb

In our example we got a = 0.496 and b = 4.389.

In this case, y is the voltage ∆V and x the OD.

To get the OD from your measured values, solve your equation for x:

# xx = ee

# ∆VV−bb

aa


Image 1:Measured OD with reference photometer against measured ∆V with openPBR
After the calibration, we measured other random samples both with our reference photometer (Expected OD) and with openPBR (Figure 2).

We also plotted the “ideal correlation”, meaning expected = measured, in order to get an idea of how good the openPBR measurements are.


Figure 2: Expected OD values from reference photometer plotted against openPBR measurements with an “ideal correlation” of x = y

From this we can conclude that, while the openPBR measurements between OD = 0 and OD = 1 are quite reliable, further calibrating points are needed in order to improve the range beyond OD = 1.

## Step 5: Thermometer:

Monitoring temperature can be very important for a lot of applications. Here we present a short do it yourself tutorial for a; low cost, online measurements. Wiring:
- Connect GND to GND
- Connect DQ to 5V(+)
- Connect VDD to digital pin 13
- Bridge DQ and VDD with a 1x 5 kohm resistor


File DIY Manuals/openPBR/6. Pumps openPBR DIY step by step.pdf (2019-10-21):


### Pumps (openPBR)

Step by Step tutorial
The pumping system of the openPBR can be used for the turbidostatic/chemo static mode and to fill and empty the cultivation vessels. They are controlled by 6 N-Channel MOSFET at 5V provided by a LM317 voltage converter. The cut outs on the back wall on the openPBR are optimized to hold the pumps without any screws.

Partlist:
- 6x DC 6V Peristaltic pump 13,99 Euro https://www.amazon.de/Acogedor-Peristaltik-Peristaltische-Fl%C3%BCssigkeiten-Dosierzus%C3%A4tze/dp/B07HHT7CD1/ref=sr_1_12?__mk_de_DE=%C3%85M%C3%85%C5%BD%C3%95%C3%91&keywords=peristaltic+pump&qid=1571504324&sr=8-12 (https://www.amazon.de/Acogedor-Peristaltik-Peristaltische-Fl%C3%BCssigkeiten-Dosierzus%C3%A4tze/dp/B07HHT7CD1?__mk_de_DE=%C3%85M%C3%85%C5%BD%C3%95%C3%91)
- 6x N-Channel MOSFET 0,67 Euro https://www.reichelt.de/mosfet-n-ch-60v-50a-110w-0-018r-to220-stp55nf06-p257486.html?r=1 (https://www.reichelt.de/mosfet-n-ch-60v-50a-110w-0-018r-to220-stp55nf06-p257486.html?r=1)
- 1x Aluminum cool bloc 0,83 Euro https://www.reichelt.de/kuehlkoerper-25-mm-alu-60-k-w-sot-32-to-220-sk-12-25-sa-32-p227995.html?&trstct=pos_0 (https://www.reichelt.de/kuehlkoerper-25-mm-alu-60-k-w-sot-32-to-220-sk-12-25-sa-32-p227995.html?trstct=pos_0)
- 1x LM317 voltage converter 0,25 Euro https://www.reichelt.de/spannungsregler-einstellbar-1-2-37-v-to-220-lm-317-220-p10458.html?r=1 (https://www.reichelt.de/spannungsregler-einstellbar-1-2-37-v-to-220-lm-317-220-p10458.html?r=1)

Total: 89,04
Solder cables to the pumps and put them into the pump holder holes in the back wall of the openPBR.


Turbidostatic/Chemo static mode:
To hold the cell density in the cultivation vessel, the Open PBR measures the cell density and controls the pumping to stay in turbidostatic conditions. On a given density one pump is pumping out media/cell culture and the second pump pumps in new media.

Electronics:
The LM317 voltage converter
- The LM317 is converting the 12V from the network adapter of the openPBR LED-panel to 5V for the pumps. You can control the voltage output of the LM317 by resistors on the ADJUST pin. To reduce the voltage from 12V to 5V you need one 1k ohm and one 330 ohm resistor. Be careful the LM317 can get very hot so it is recommended to attach a proper cooling bloc.
- Connect INPUT to 12V(+) white cable.
- Connect on 330 ohm resistor from ADJUST to OUTPUT.
- Connect one 330 ohm and one 1kohm resistor in row to the 12V (-).
- Connect a cable (violet) to the lane you want to have 5V (+) on.


More information to the LM317 you can find here: http://www.learningaboutelectronics.com/Articles/LM317-resistor-and-voltagecalculator.php#answer1 (http://www.learningaboutelectronics.com/Articles/LM317-resistor-and-voltage-calculator.php#answer1)

N-Chanel MOSFET
- Connect G (Gate) with a 100 ohm resistor to your Arduino digital pins according to the position of the pump e.g. Left (Out/In), Middle (Out/In), Right (Out/In). Here blue and yellow cable.
- Connect S (Source) to ground (-).
- Connect D (Drain) to each (-) of your pump.
- Connect the 5V (+) of each pump to the 5V lane of the LM317.


The complete wiring and circuit diagram of the openPBR you find in: DIY Manual on GitHub
The software to control the pumps you find in the openPBR_control software.

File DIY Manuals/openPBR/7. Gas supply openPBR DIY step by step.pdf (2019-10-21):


### Gas supply (openPBR)

The gas supply system of the openPBR provides the setup with controllable gas flow up to 250 l/h. Chaotic mixing of the culture is solely provided by the gas pressure. The gas pressure can be regulated by rotameters. A magnet valve is turning off the gas supply while measuring the OD.

Pricelist:
- 1x 5 Watt Gas pump 250 l/h, 19,99 Euro https://www.amazon.de/dp/B004PGVHCA/ref=twister_B01CHWCMY0?_encoding=UTF8&psc=1 (https://www.amazon.de/dp/B004PGVHCA/ref=twister_B01CHWCMY0?_encoding=UTF8&psc=1)
- 3x Rotameter 1-5l/h 11,66 Euro https://www.amazon.de/Acryl-Luft-Sauerstoffgas-Durchflussmesser-Regelventil-Messung-Regelung-Gasdurchflusses/dp/B07WNWKV37/ref=sr_1_1?__mk_de_DE=%C3%85M%C3%85%C5%BD%C3%95%C3%91&keywords=rotameter+luft&qid=1571527908&s=diy&sr=1-1 (https://www.amazon.de/Acryl-Luft-Sauerstoffgas-Durchflussmesser-Regelventil-Messung-Regelung-Gasdurchflusses/dp/B07WNWKV37?__mk_de_DE=%C3%85M%C3%85%C5%BD%C3%9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)
- x2 Gas valve stainless steel, 2,49 Euro https://www.gispo.de/Luftventil-METALL-mit-2-stufenlos-regelbare-Abgaenge-Anschluss-4mm (https://www.gispo.de/Luftventil-METALL-mit-2-stufenlos-regelbare-Abgaenge-Anschluss-4mm)
- Magnet Valve 12 V DC 10,49 https://www.amazon.de/Kunststoff-Magnetventil-Wasser-Normalerweisegeschlossen/dp/B019W349HU/ref=sr_1_1?ie=UTF8&qid=1547647761&sr=8-1&keywords=6mm+magnetventil (https://www.amazon.de/Kunststoff-Magnetventil-Wasser-Normalerweise-geschlossen/dp/B019W349HU)
Total: 70,49 Euro

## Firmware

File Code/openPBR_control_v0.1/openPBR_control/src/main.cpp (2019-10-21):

/**
* #########################
* # Humbold University zu Berlin
* # iGEM 2019 on Chlaydomonas cultivation
*
* #########################
* # @version  0.5
* # @platform  arduino AT Mega 2560
* # @clock  16mHz
* # @created  20190614
* # @changed  2011018
* # @user

      epicness
      tet
*
* #########################
* # selftest, rining wires, light on big to grow, break in for sensoring
* # grow-30sec, break-1sec
*
* #########################
*/
//#####################################################################
// general import declaration
#include <Arduino.h>

//#####################################################################
// pcb wiring - input analog of sensors
int sensorPinMainVCC   = A0;    // vcc level in volt of 5 Volt system
int sensorPinCurrent1  = A1;    // current used via shunt in mV/
int irSensorLeft = A2;          // opt 101  sense 680nm in mV
int sensorPinCurrent2  = A3;    // current used via shunt in mV/
int irSensorMiddle = A4;        // opt 101  sense 680nm in mV
int sensorPinCurrent3  = A5;    // current used via shunt in mV/
int irSensorRight = A6;         // opt 101  sense 680nm in mV   // Water Temp. Sensor DS18B20

// pcb wiring - input digital

 int whitePin = 3;
 int redPin   = 4;
 int greenPin = 5;
 int bluePin  = 6;

 int pumpLeftIn    = 8;
 int pumpLeftOut   = 7;
 int pumpMiddleIn = 10;
 int pumpMiddleOut = 9;
 int pumpRightIn  = 12;
 int pumpRightOut = 11;

 int sensorPinTempSense = 14;
 int airValve = 13;

 //
  int irLEDLeft   = 15;
  int irLEDMiddle = 16;
  int irLEDRight  = 17;

//#####################################################################
//  member variables - variable, to calc and screw
int analogRead0 = 0;     // vcc main supply of the system
int analogRead1 = 0;     // opt101 current value
int readLeftSensor = 0;  // opt101 sensor value
int analogRead3 = 0;     // opt101 current value
int readMiddleSensor = 0;// opt101 sensor value
int analogRead5 = 0;     // opt101 current value
int readRightSensor = 0; // opt101 sensor value
int analogRead7 = 0;     // no function yet

int digitalRead0 = 0; // vcc main supply
int digitalRead1 = 0; //
int digitalRead2 = 0; //
int digitalRead3 = 0; // WhiteLED
int digitalRead4 = 0; // RedLED
int digitalRead5 = 0; // GreenLED
int digitalRead6 = 0; // BlueLED
int digitalRead7 = 0; // pumpLeftOut
int digitalRead8 = 0; // pumpLeftIn
int digitalRead9 = 0; // pumpMiddleOut
int digitalRead10 = 0;// pumpMiddleIn
int digitalRead11 = 0;// pumpRightOut
int digitalRead12 = 0;// pumpRightIn
int digitalRead13 = 0;// airValve to stop gas flow to the chambers
int digitalRead14 = 0;

int inByte = 0;         // incoming serial byte

int roundCycle = 0; // number of measurments


int brightnessWhite = 0; // value between 0 und 255 – for intensity of white LEDs
int brightnessRed = 0; // value between 0 und 255 – for intensity of red LEDs
int brightnessGreen = 0; // value between 0 und 255 – for intensity of green LEDs
int brightnessBlue = 0; // value between 0 und 255 – for intensity of blue LEDs
int airValveStatus = 0; // dont touch!
//#####################################################################
// member variables - timing
unsigned long previousMillis = 0;   // will store last time
const long interval = 10*60*1000;        // 10 minutes x 60 sec * 1000 milli
const int pumpTime = 5000; // time the pump is running

//#####################################################################

/**
 * shift the value to the external module ( MOSFET )
 */
void setColor() {
  analogWrite(redPin, brightnessRed);
  analogWrite(greenPin,brightnessGreen);
  analogWrite(bluePin, brightnessBlue);
  analogWrite(whitePin, brightnessWhite);
  analogWrite(airValve, airValveStatus);
  delay(100);
}

/**
##########################################################################
 * set white, red and blue to 255 and green to 50;
 */
 void setAllLLightOn() {
    brightnessWhite = 255;
    brightnessRed = 255;
    brightnessGreen = 255;
    brightnessBlue = 255;
    airValveStatus = 0;
    setColor();
    delay(100);
 }

 /**
  * set white, red and blue to 255 and green to 50;
  */
  void setLightOff() {
     brightnessWhite = 0;
     brightnessRed = 0;
     brightnessGreen = 0;
     brightnessBlue = 0;
     airValveStatus = 0;
     setColor();
     delay(100);

  }


/**
 * set white, red and blue to your wished intensity and color ;
 */
 void setGrowLight() {
    brightnessWhite = 150;
    brightnessRed = 150;
    brightnessGreen = 150;
    brightnessBlue = 150;

    airValveStatus = 255;
    setColor();
 }



/**
* prepare and init variables and io procedure
*/
void setup() {

  // monitoring on a remote computer
  Serial.begin(9600);
  while (!Serial) {
    ; // getReadyStateLike
  }

  delay(2222);  // time to get upset done

  // ready we guess....
  if (Serial.available() == 0 && Serial.availableForWrite() > 0) { // ready for serial output
    //Serial.available()
    Serial.print("SERIAL[");
    Serial.print(Serial.available());
    Serial.print("|");
    Serial.print(Serial.availableForWrite());
    Serial.print("|");
    Serial.print(Serial.getTimeout());
    Serial.println("]");
    delay(Serial.getTimeout()*1.41);

  }

  // gpio - input // Arduino pin selction

  pinMode(sensorPinMainVCC, INPUT); // analog0
  pinMode(sensorPinCurrent1, INPUT); // analog1
  pinMode(irSensorLeft, INPUT); // analog3
  pinMode(sensorPinCurrent2, INPUT); // analog4
  pinMode(irSensorMiddle, INPUT); // analog5
  pinMode(sensorPinCurrent3, INPUT); // analog6
  pinMode(irSensorRight, INPUT); // analog7
  pinMode(sensorPinTempSense, INPUT); // digital13
  // gpio - output
  pinMode(whitePin, OUTPUT);
  pinMode(redPin, OUTPUT);
  pinMode(greenPin, OUTPUT);
  pinMode(bluePin, OUTPUT);
  pinMode(pumpLeftIn, OUTPUT);
  pinMode(pumpLeftOut, OUTPUT);
  pinMode(pumpMiddleIn, OUTPUT);
  pinMode(pumpMiddleOut, OUTPUT);
  pinMode(pumpRightIn, OUTPUT);
  pinMode(pumpRightOut, OUTPUT);
  pinMode(airValve, OUTPUT);

  pinMode(irLEDLeft, OUTPUT);
  pinMode(irLEDMiddle, OUTPUT);
  pinMode(irLEDRight, OUTPUT);


  // informing the serial monitor, which source file was used ....
  Serial.println("using file for this project: OpenPBR-0.4.cpp");
//####################
  // log header
  Serial.println("INIT[roundCycle,Vcc,Vin LeftChamber,Vout LeftChamber ,Vin MiddleChamber,Vout MiddleChamber,Vin rightChamber,Vout rightChamber,Temp.]");

  Serial.print("INTERVAL,");// first line in log for interval
  Serial.print(interval);
  Serial.println(",");
//#####################

  Serial.print("INPUTPORT[");
  Serial.print(millis());
  Serial.print(",");
  Serial.print(sensorPinMainVCC);
  Serial.print(",");
  Serial.print(sensorPinCurrent1); //Vin LeftChamber
  Serial.print(",");
  Serial.print(sensorPinCurrent2); //Vin MiddleChamber
  Serial.print(",");
  Serial.print(sensorPinCurrent3); //Vin rightChamber
  Serial.print(",");
  Serial.print(irSensorLeft); //Vout LeftChamber
  Serial.print(",");
  Serial.print(irSensorMiddle); //Vout MiddleChamber
  Serial.print(",");
  Serial.print(irSensorRight); //Vout rightChamber
  Serial.print(",");
  Serial.print(sensorPinTempSense);
  Serial.println(",");
/*
//this could be used for button control in future
  Serial.print("OUTPUTPORT[");
  Serial.print(ledPWR);
  Serial.print("|");
  Serial.print(ledRDY);
  Serial.print("|");
  Serial.print(ledBSY);
  Serial.println("]");
*/

Serial.print("UPDATE[");
Serial.print(interval);
Serial.println(",");

  // led check, on and off
  Serial.println("running all led to ON");
  delay(2222);
  setAllLLightOn();
  delay(2222);
  Serial.println("running all led to OFF");
  setLightOff();
  delay(2222);


  Serial.println("SETUP[done]");
}


//#####################################################################
// from here on running code for non blocking behaviour// ab hier echtes programm
//#####################################################################


/**
* read values from wired inputs
* send data via serial to host computer, for logging
*/
void doTheLogging() { //logging of sensor values
  //if ( isItTime == 1 ) {
    // get incoming byte:
    inByte = Serial.read(); // start serial monitor
    //#####################################################################
    analogRead0 = analogRead(sensorPinMainVCC); //real values
    analogRead1 = analogRead(sensorPinCurrent1);
    //readLeftSensor = analogRead(irSensorLeft);
    analogRead3 = analogRead(sensorPinCurrent2);
    //readMiddleSensor = analogRead(irSensorMiddle);
    analogRead5 = analogRead(sensorPinCurrent3);
    //readRightSensor = analogRead(irSensorRight);


    // read switch, map it to 0 or 255 //for buttons in future
  //  digitalRead0 = map(digitalRead(digitalPinInput), 0, 1, 0, 255); // for buttons in future
    //#####################################################################
    // send sensor values:
    Serial.print("DATA ,");
    Serial.print(roundCycle);
    Serial.print(",");
    Serial.print(analogRead0 * ( 5.0 / 1023 )); // divide 5V through 1023
    Serial.print(",");
    Serial.print(analogRead1 * ( 5.0 / 1023 ));
    Serial.print(",");
    Serial.print(readLeftSensor * ( 5.0 / 1023 ));
    Serial.print(",");
    Serial.print(analogRead3 * ( 5.0 / 1023 ));
    Serial.print(",");
    Serial.print(readMiddleSensor * ( 5.0 / 1023 ));
    Serial.print(",");
    Serial.print(analogRead5 * ( 5.0 / 1023 ));
    Serial.print(",");
    Serial.print(readRightSensor * ( 5.0 / 1023 ));
    Serial.print(",");
    Serial.print(digitalRead13);// temp senseor
    Serial.println(",");
  //} else {
    // nothing
    // Serial.println("SERIAL[UNRESOLVED]");
    // @todo could count the unused case here :/
//}
    roundCycle++; // number of measurments  +1
}


/**
//for buttons
* timer check and update
* blinks then
*/
void checTimeAndLog(){ //
  unsigned long currentMillis = millis(); // holt laufzeit seit setup()
  if ((currentMillis - previousMillis) >= interval) { // es so weit

    // save time
    previousMillis = currentMillis;
    setLightOff();
    delay(500);
    doTheLogging();
    delay(500);
  } else {
    setGrowLight();
  }

//  } else {
    // come back later and use above
//  }

}

/**
  * switch ir led on, read value from opt101 sensor, switch ir led off
  */
void measureDensity(){
    // put ir led on
    digitalWrite(irLEDLeft, HIGH);
    digitalWrite(irLEDMiddle, HIGH);
    digitalWrite(irLEDRight, HIGH);



    delay(1000);    // give the sensor some time, to swing in

    // measure density with sesor opt101
     readLeftSensor = analogRead(irSensorLeft);
     readMiddleSensor = analogRead(irSensorMiddle);
     readRightSensor = analogRead(irSensorRight);

     digitalWrite(irLEDLeft, LOW);
     digitalWrite(irLEDMiddle, LOW);
     digitalWrite(irLEDRight, LOW);



     delay(1000);   // wait, till measruing is done
  // switch ir led OFF
}
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
